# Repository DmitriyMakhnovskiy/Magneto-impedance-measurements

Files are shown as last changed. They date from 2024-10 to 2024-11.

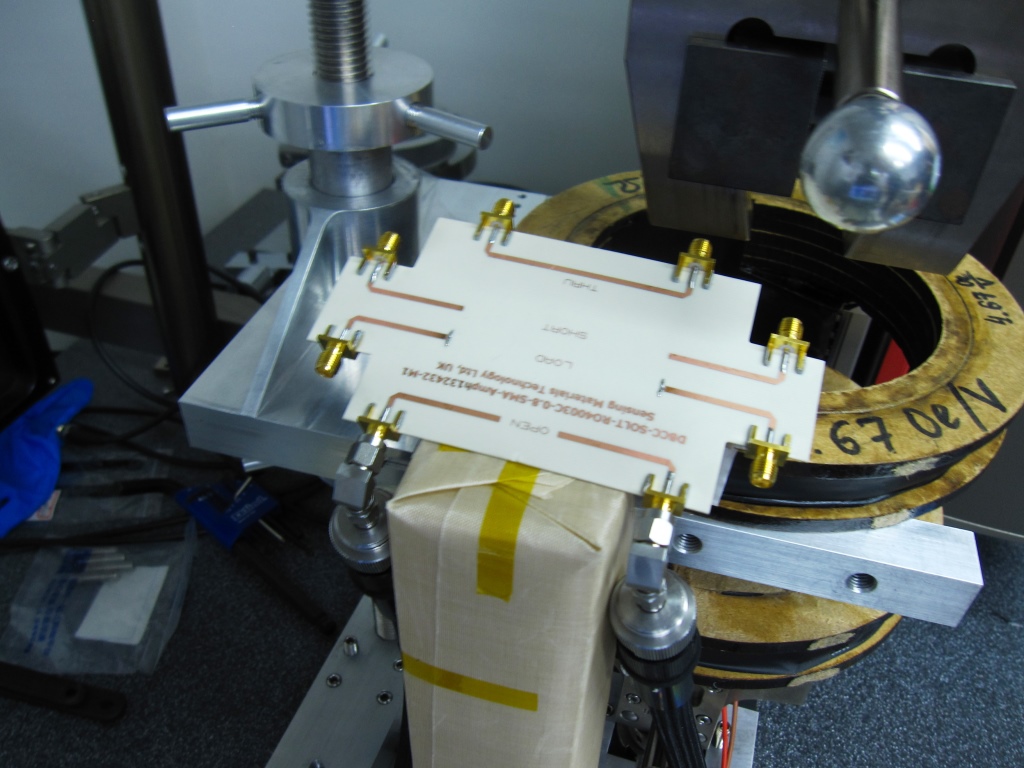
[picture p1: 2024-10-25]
Stress-impedance and Zwick-Roell Award/Design gallery/IMG_7724.JPG

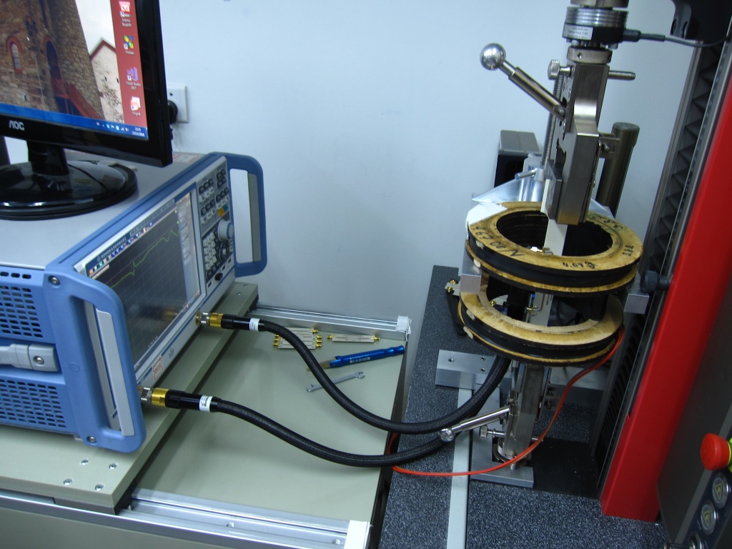
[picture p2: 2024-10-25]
Stress-impedance and Zwick-Roell Award/Design gallery/IMG_7733.JPG

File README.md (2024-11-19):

# Magneto-impedance_measurements
Measuring magneto-impedance in ferromagnetic wires subjected to external stimuli such as magnetic field, tensile stress, and temperature

See the report in the file "Report_Multi-stage calibration for impedance measurements.pdf". 

SUMMARY

This project focuses on measuring surface impedance in ferromagnetic wires, a crucial aspect in developing materials with specific microwave properties for applications in sensors and metamaterials. We present a broadband impedance measurement technique operational up to 15 GHz, designed to simplify the characterization of ferromagnetic microwires, which exhibit unique magnetic and conductive behaviors influencing electromagnetic scattering. We develop customized printed circuit board cells (see the folder Rogers' PCB cells) and a multi-stage calibration process that enables flexibility in testing under different external stimuli, such as magnetic fields, temperature, and mechanical stress.

KEY CONTRIBUTIONS

  Broadband Measurement Technique: Establishes a method for accurate impedance measurements up to 15 GHz, crucial for analyzing microwire-based composites.

  PCB Calibration Cells: Develops PCB cells for precise impedance measurements, accounting for factors like temperature and mechanical stress.

  Numerical Simulation Compatibility: Enables use of experimentally derived impedance values in computational simulations, supporting advanced material design.

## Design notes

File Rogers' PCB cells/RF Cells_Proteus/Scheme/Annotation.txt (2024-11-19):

Dogbone20
Material:RO4003C
Thickness: 0.8mm
Layers: Top copper, bottom copper, top silk
Mech3 layer repeats the board edge.

Sensing Materials Technology Ltd
contact@sensmattech.co.uk

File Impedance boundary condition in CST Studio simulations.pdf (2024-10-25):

# Use of the impedance boundary condition in CST Studio simulations

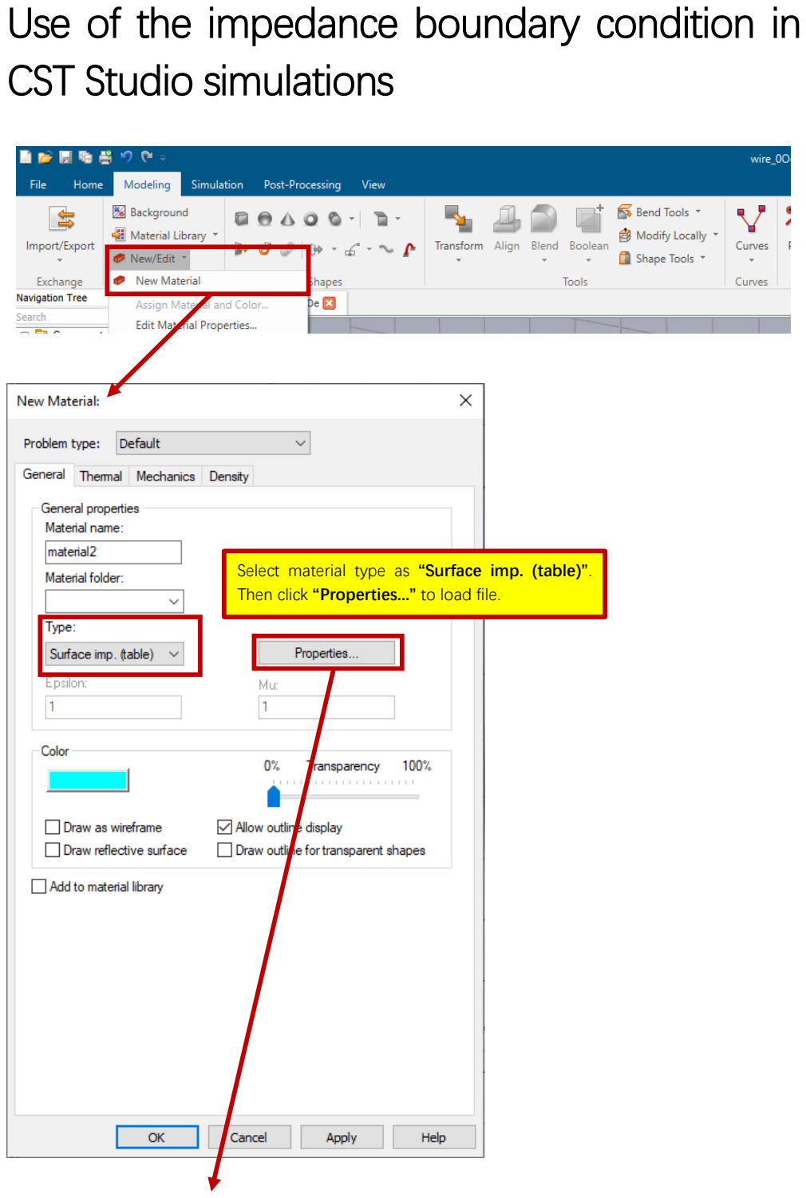
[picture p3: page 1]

Select material type as “Surface imp. (table)”. Then click “Properties...” to load file.

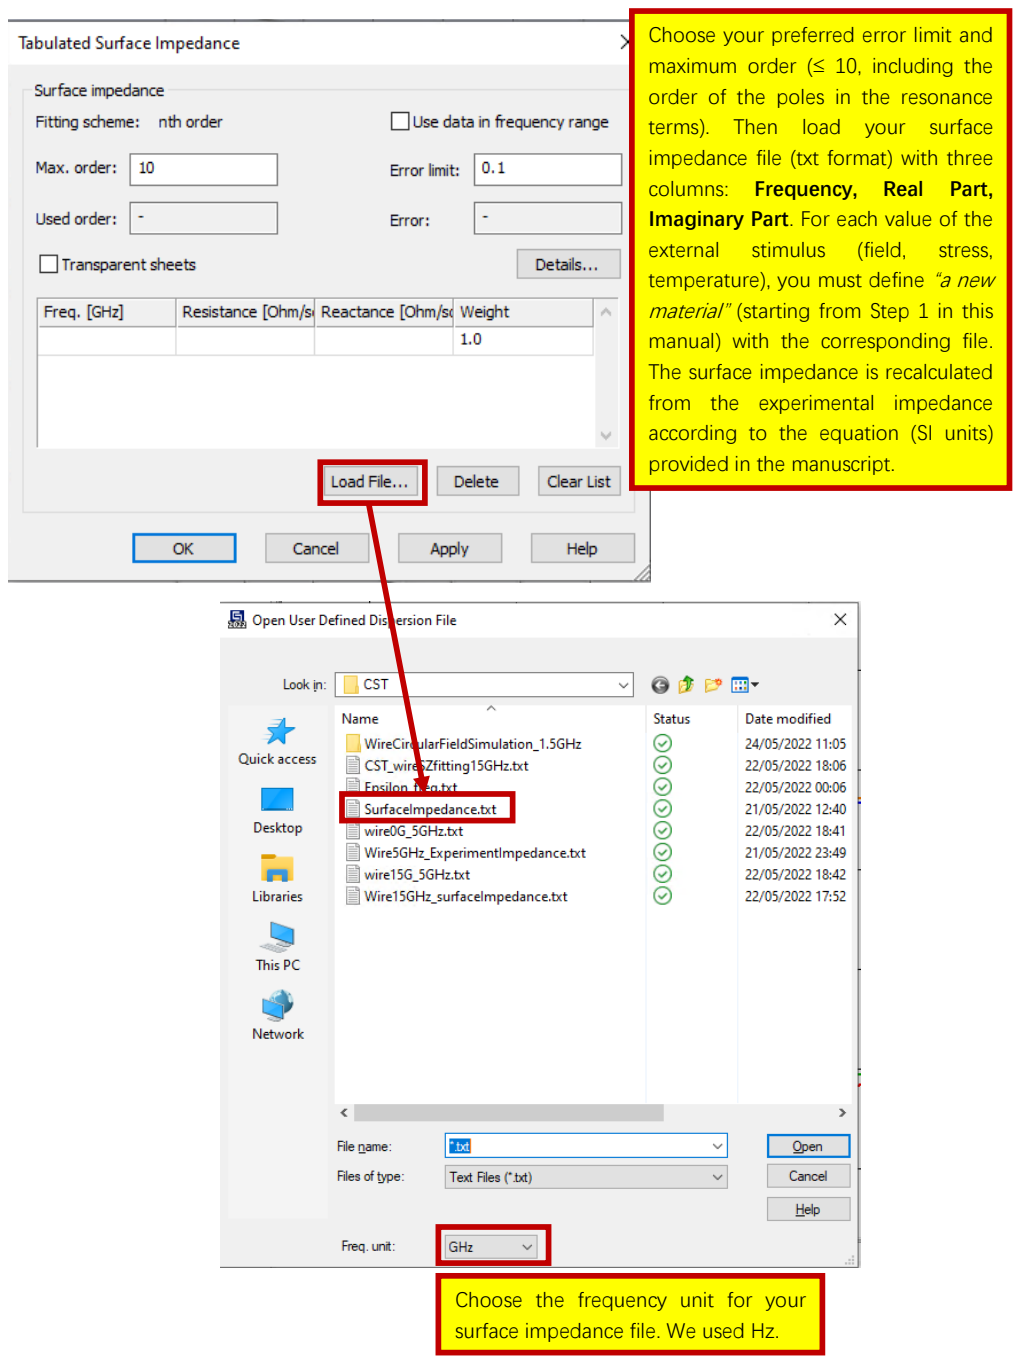
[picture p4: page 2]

Choose the frequency unit for your surface impedance file. We used Hz.

Choose your preferred error limit and maximum order (≤ 10, including the order of the poles in the resonance terms). Then load your surface impedance file (txt format) with three columns: Frequency, Real Part, Imaginary Part. For each value of the
external | stimulus | (field, | stress,
temperature), you must define “a new material” (starting from Step 1 in this manual) with the corresponding file. The surface impedance is recalculated from the experimental impedance according to the equation (SI units) provided in the manuscript.

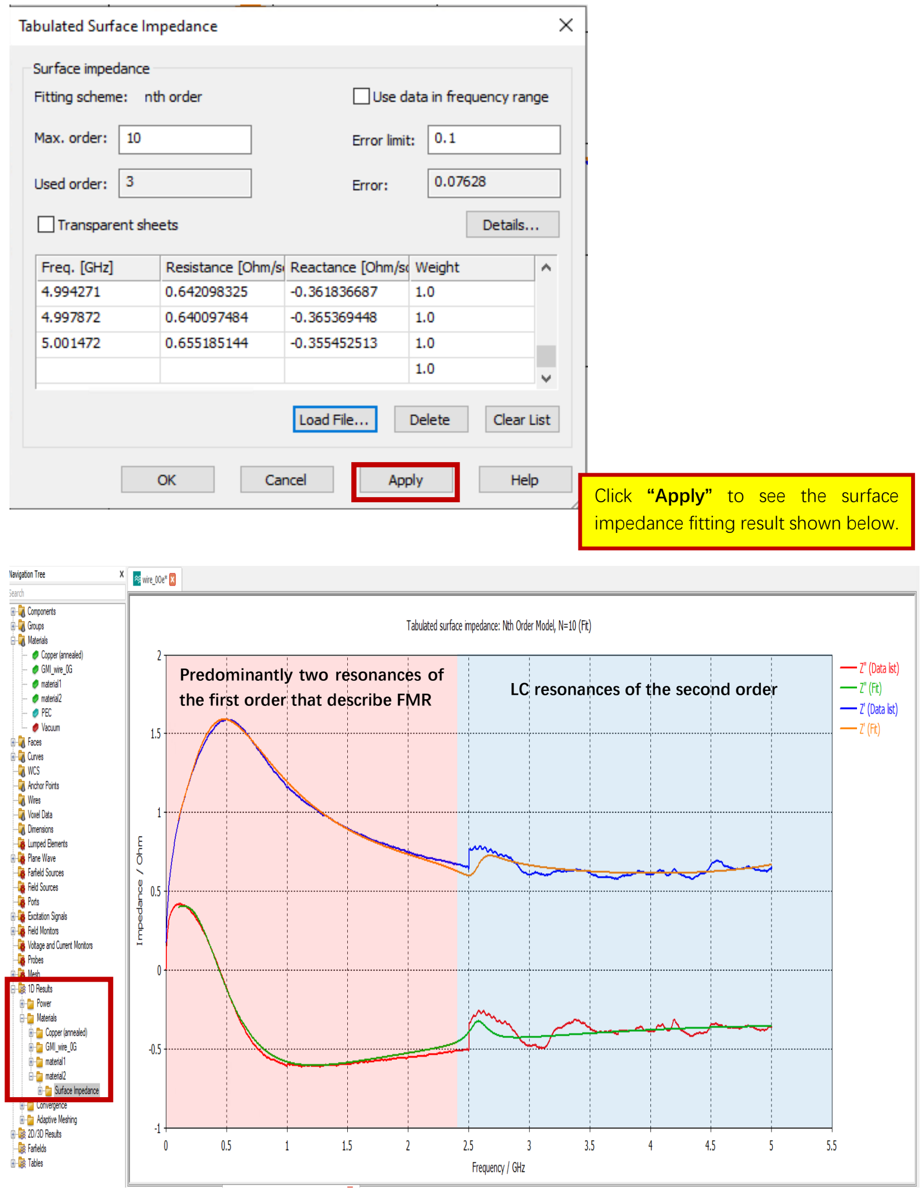
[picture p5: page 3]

Click “Apply” to see the surface impedance fitting result shown below.

Predominantly two resonances of
the first order that describe FMR | LC resonances of the second order

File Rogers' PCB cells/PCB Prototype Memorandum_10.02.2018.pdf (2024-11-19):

# PCB Prototype Memorandum

## Project

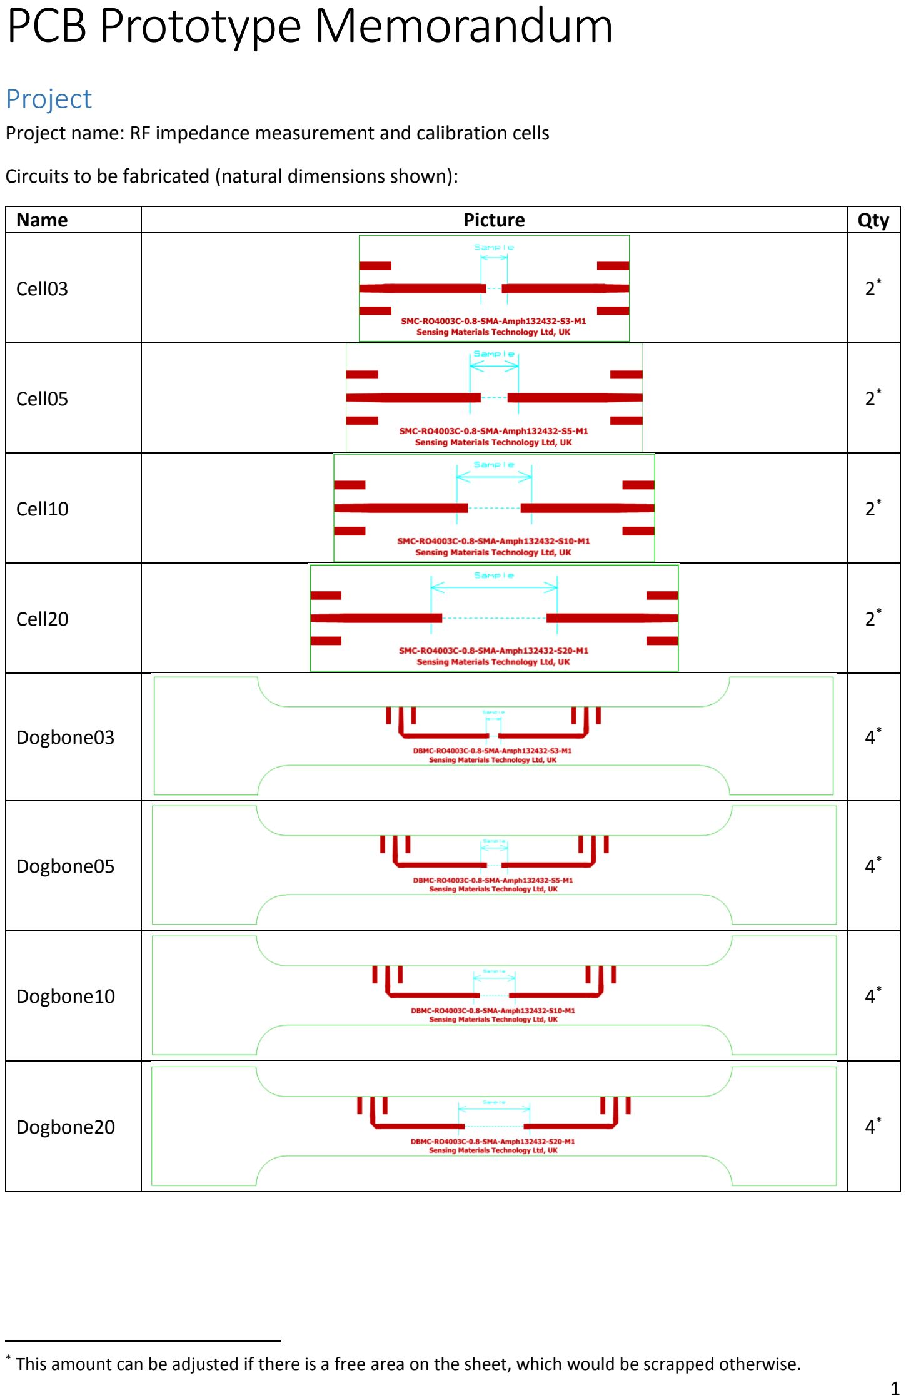
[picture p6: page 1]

Project name: RF impedance measurement and calibration cells

Circuits to be fabricated (natural dimensions shown):

Name | Picture | Qty
Cell03 | | 2 *
Cell05 | | 2 *
Cell10 | | 2 *
Cell20 | | * 2
Dogbone03 | | 4 *
Dogbone05 | | * 4
Dogbone10 | | 4 *
Dogbone20 | | 4 *

* This amount can be adjusted if there is a free area on the sheet, which would be scrapped otherwise.

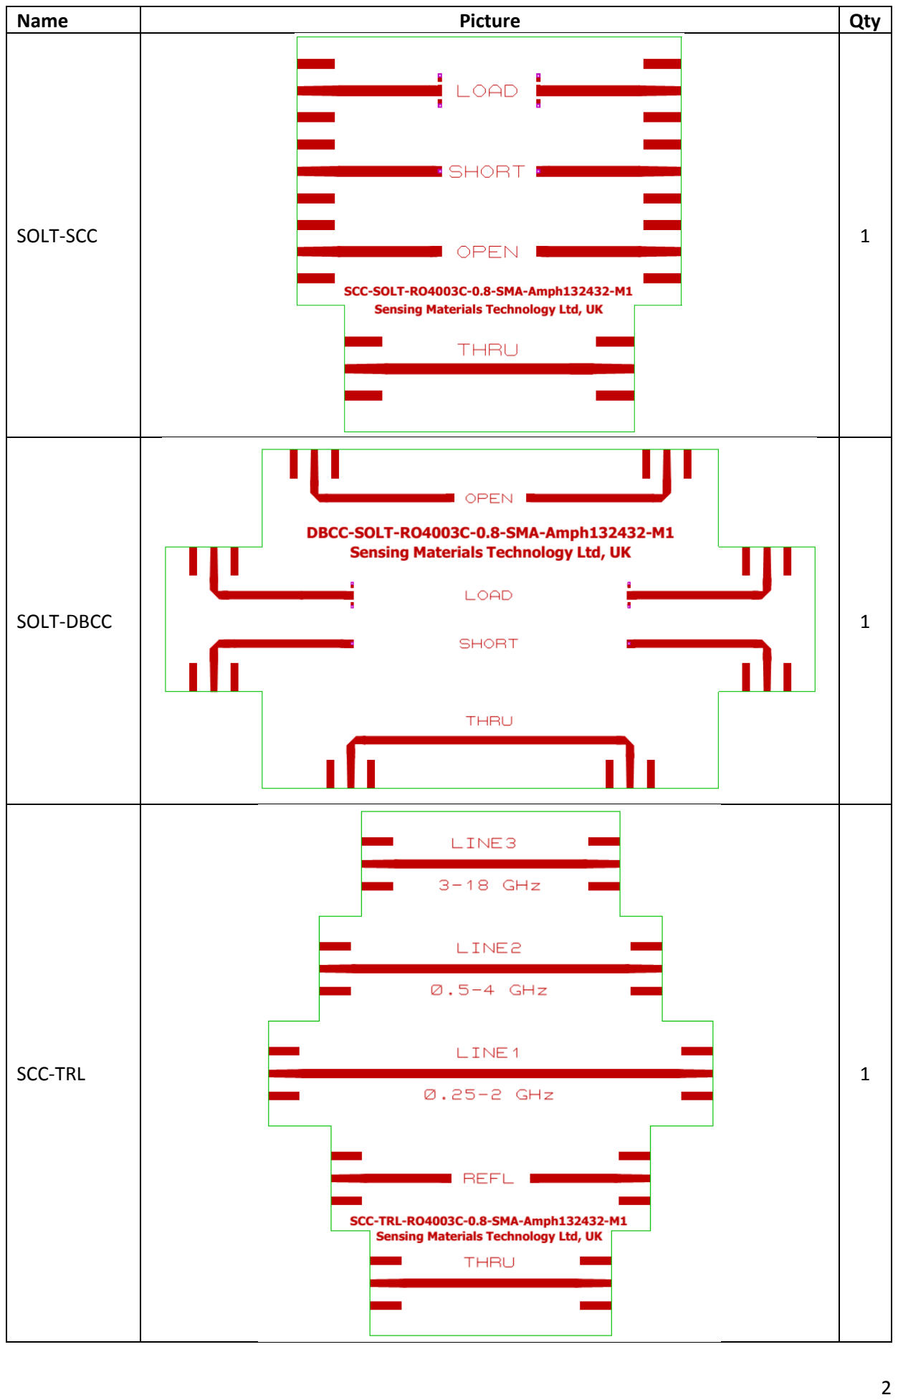
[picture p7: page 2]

Name | Picture | Qty
SOLT-SCC | | 1
SOLT-DBCC | | 1
SCC-TRL | 1

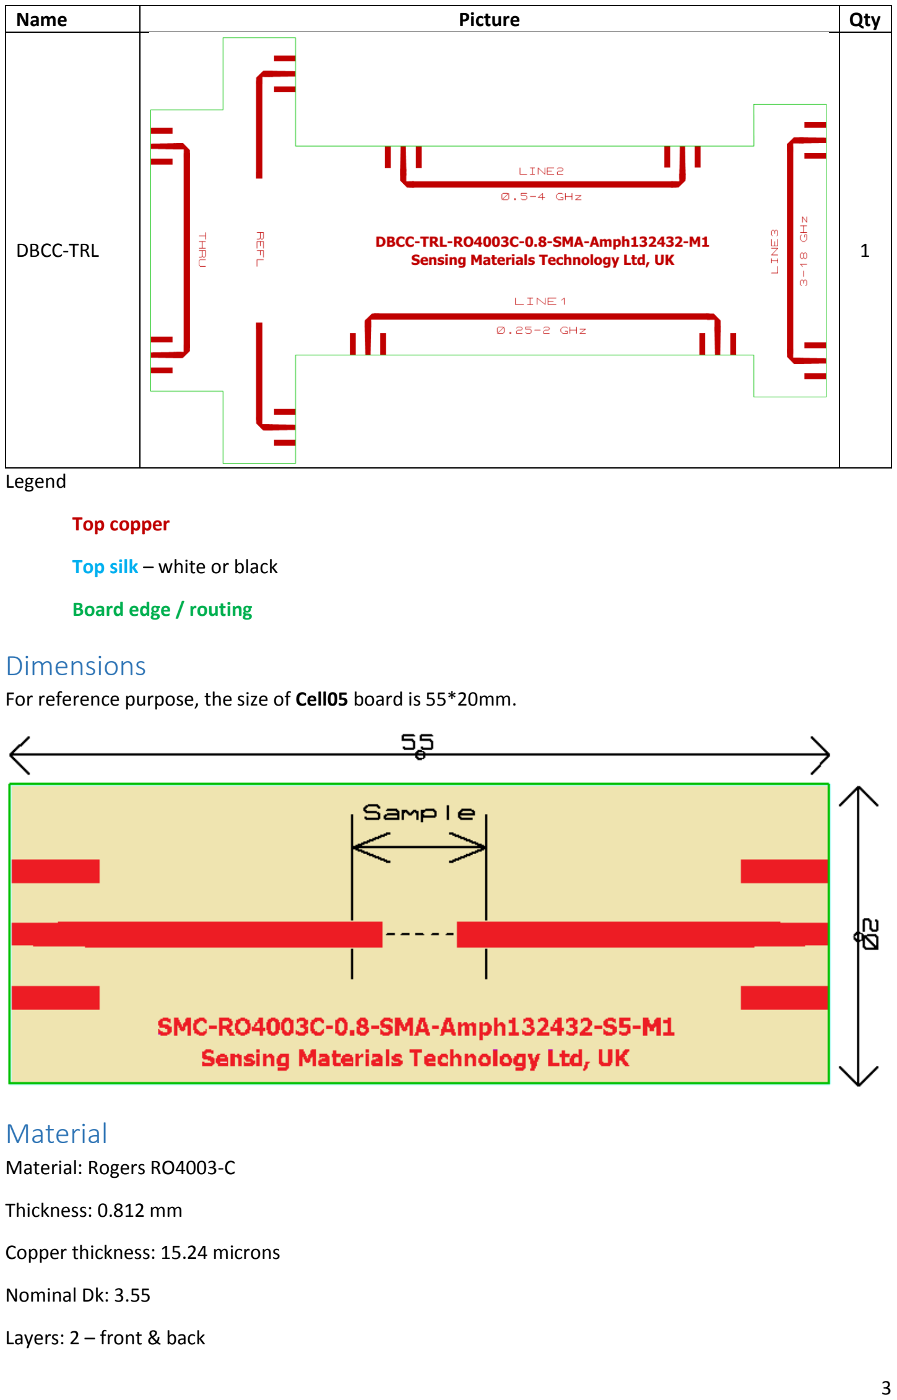
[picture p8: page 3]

Name | Picture | Qty
DBCC-TRL | | 1

Legend

Top copper

Top silk – white or black

Board edge / routing

## Dimensions

For reference purpose, the size of Cell05 board is 55*20mm.

## Material

Material: Rogers RO4003-C

Thickness: 0.812 mm

Copper thickness: 15.24 microns

Nominal Dk: 3.55

Layers: 2 – front & back

## PCB Fabrication

Surface finish: none

Silkscreen: single sided, front only, color depends on the color of the material: black for yellow or white for green.

Solder mask: none

Peelable mask: none

Carbon print: none

Carbon finish: none

Min. track width: 0.61 mm

Min track gap: standard

Vias: 0.3mm, plated, through

Shape: special contour routing

Electrical checks: not required

Data format: Gerber RS274X / RS264D, metric

## Panelizing

Gerber files for individual circuits would be provided. Panelizing is highly desirable.

## Other

Lead-time: 2 weeks

Delivery to: Plymouth, UK

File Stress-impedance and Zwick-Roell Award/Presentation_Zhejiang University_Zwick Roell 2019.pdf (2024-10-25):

# Integration of microwave and mechanical stress measurements:

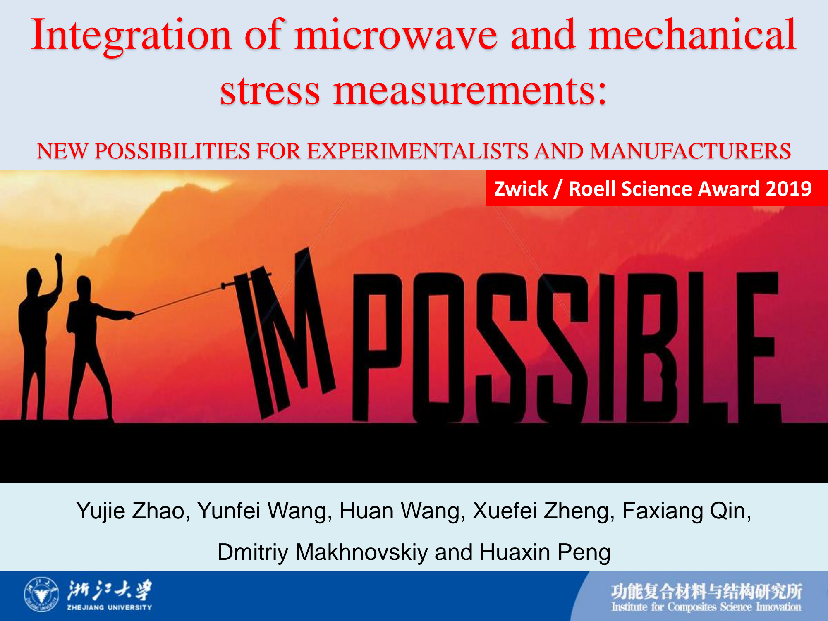
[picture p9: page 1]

NEW POSSIBILITIES FOR EXPERIMENTALISTS AND MANUFACTURERS

Yujie Zhao, Yunfei Wang, Huan Wang, Xuefei Zheng, Faxiang Qin,

Dmitriy Makhnovskiy and Huaxin Peng

Zwick / Roell Science Award 2019

# Content

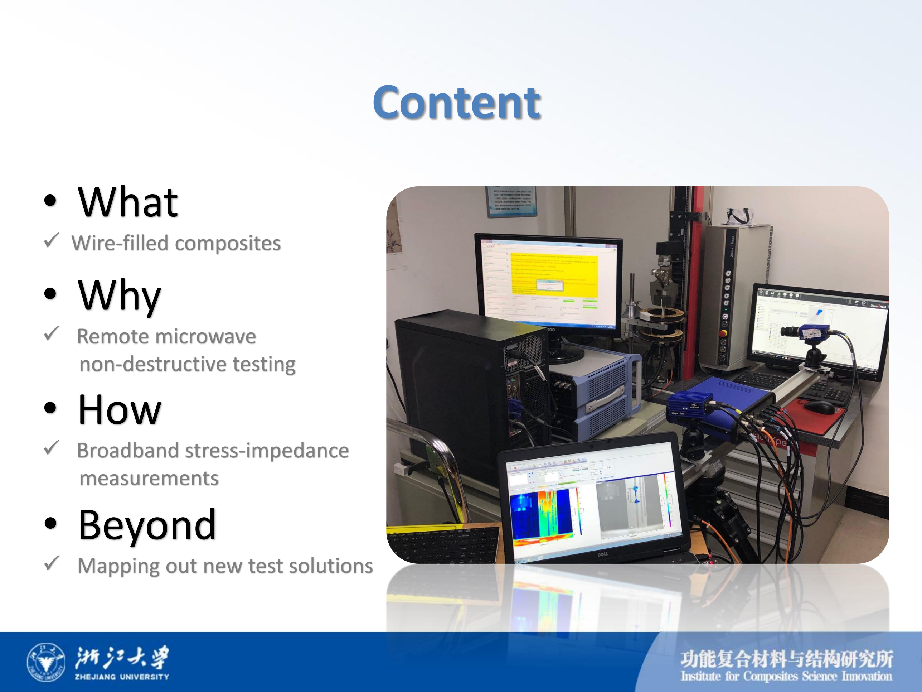
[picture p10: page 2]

# - What

✓ Wire-filled composites

# - Why

✓ Remote microwave
non-destructive testing

# - Beyond

✓ Mapping out new test solutions

# - How

✓ Broadband stress-impedance measurements

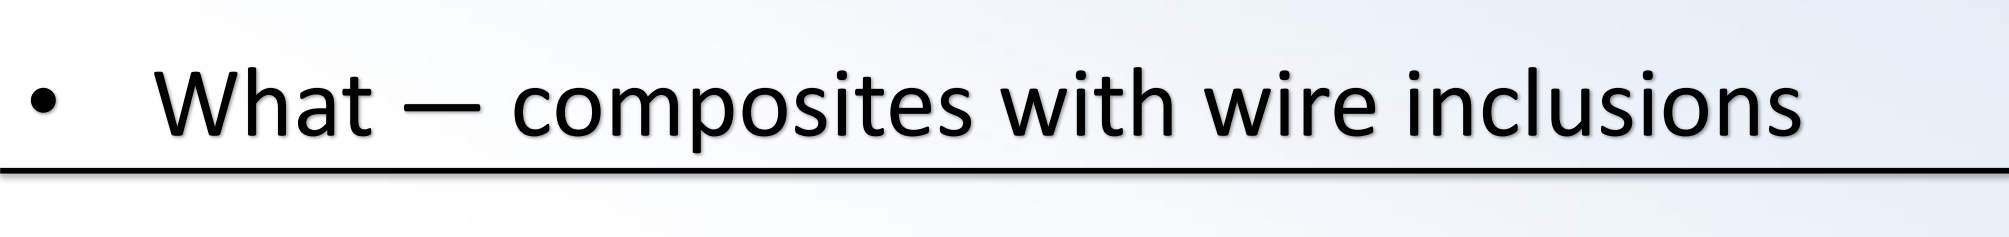
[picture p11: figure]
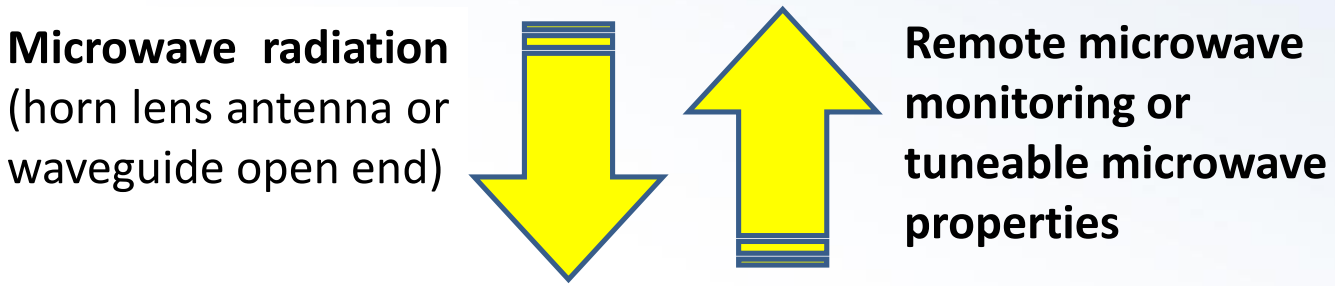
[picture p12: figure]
Microwave radiation (horn lens antenna or waveguide open end); Remote microwave monitoring or tuneable microwave properties
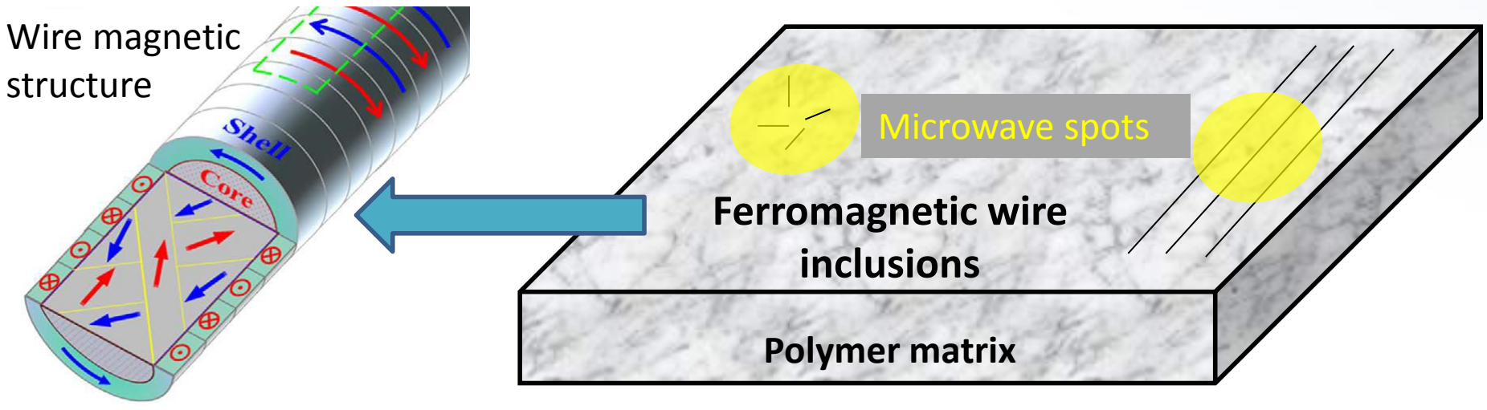
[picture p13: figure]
Ferromagnetic wire inclusions; Polymer matrix; Microwave spots; Wire magnetic structure

### External stimuli: magnetic field, mechanical stress, and temperature

# - What — composites with wire inclusions

# - Why—non-destructive evaluation technique

## Antenna

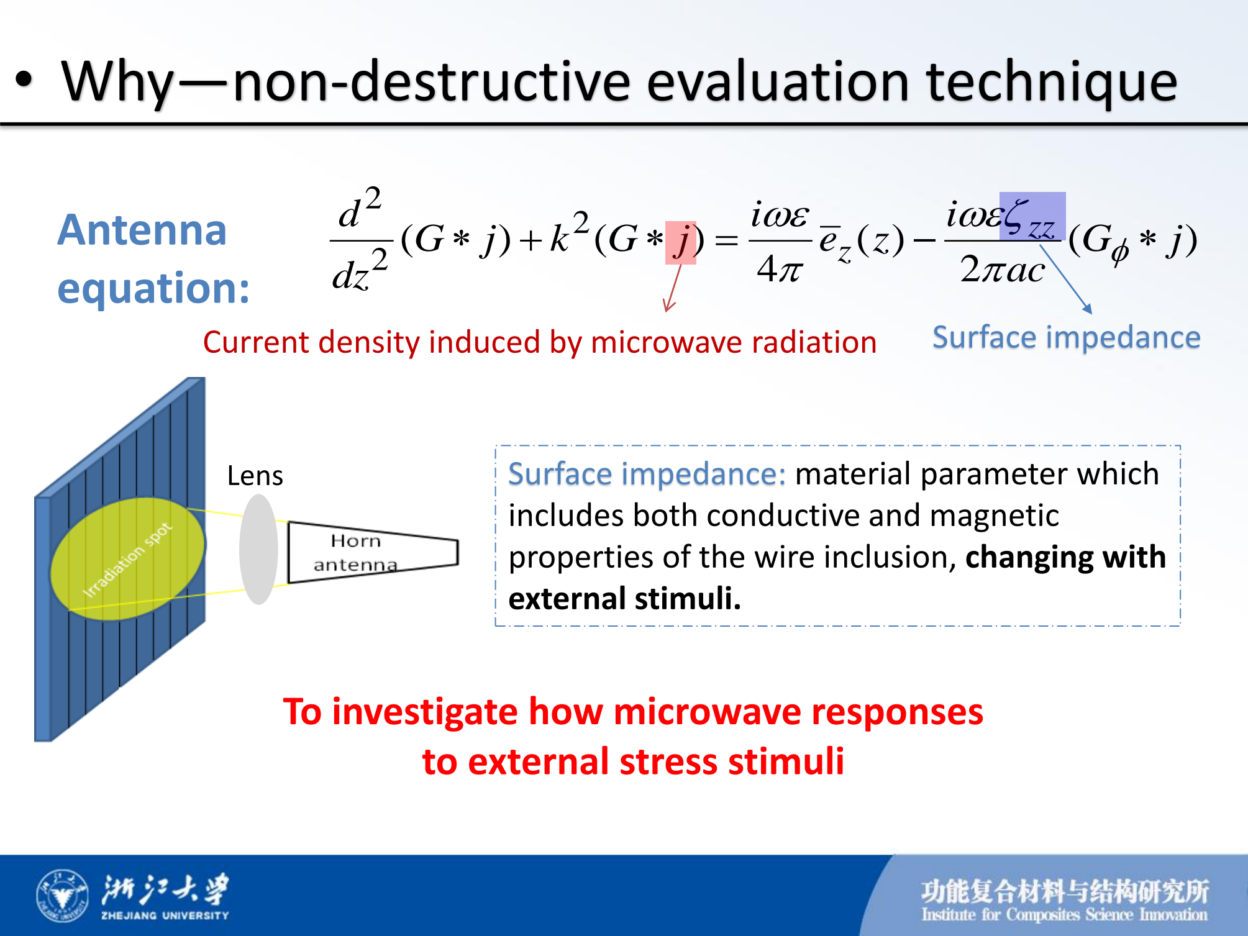
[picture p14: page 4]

2
2
2
( | ) | ( | ) | ( ) | ( | )
4 | 2

zz
z
d | i | i G j | k G | j | e z | G | j
dz | ac

φ

ωε | ωεζ
π | π
* | + | * | = | − | *
Current density induced by microwave radiation | Surface impedance
Lens | Surface impedance: material parameter which includes both conductive and magnetic properties of the wire inclusion, changing with external stimuli.

### To investigate how microwave responses to external stress stimuli

## equation:

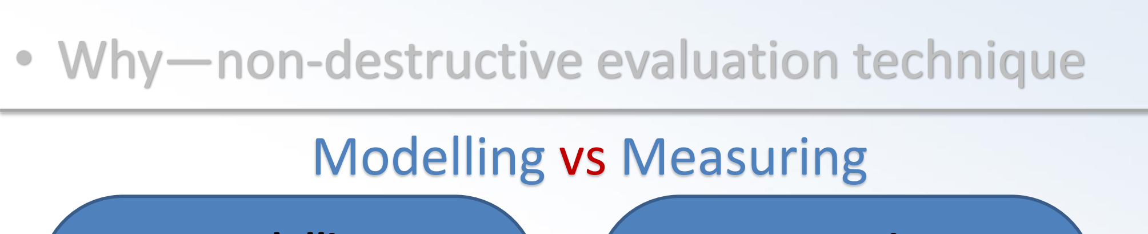
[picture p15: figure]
Modelling vs Measuring

# - Why—non-destructive evaluation technique

## Modelling

? ?

- Complicated magnetic domain structure
- Existing models are not
sufficiently accurate for
microwave scattering properties of composite structures

## Measuring

√ √

- Broad frequency range
calibration and measurement technique
- Recalculation into surface impedance by
- Develop scattering theory based on the antenna equation

9
( , , ) 10 | ( , , ) / (2 )
stress, | magnetic field
zz | H | aZ | H | cl
H
ζ ω | σ | ω | σ
σ

=
− | −

# - How—measurement system

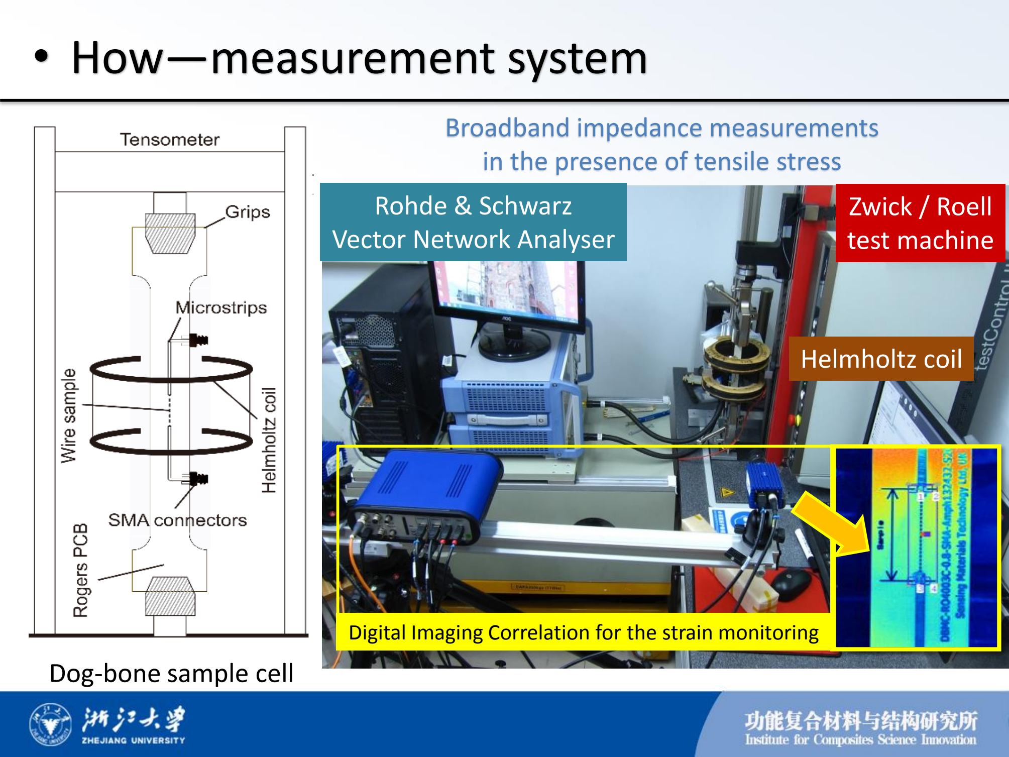
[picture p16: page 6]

Broadband impedance measurements in the presence of tensile stress Zwick / Roell
test machine

Rohde & Schwarz
Vector Network Analyser

Helmholtz coil

Dog-bone sample cell

Digital Imaging Correlation for the strain monitoring

# - How— RF calibration technique

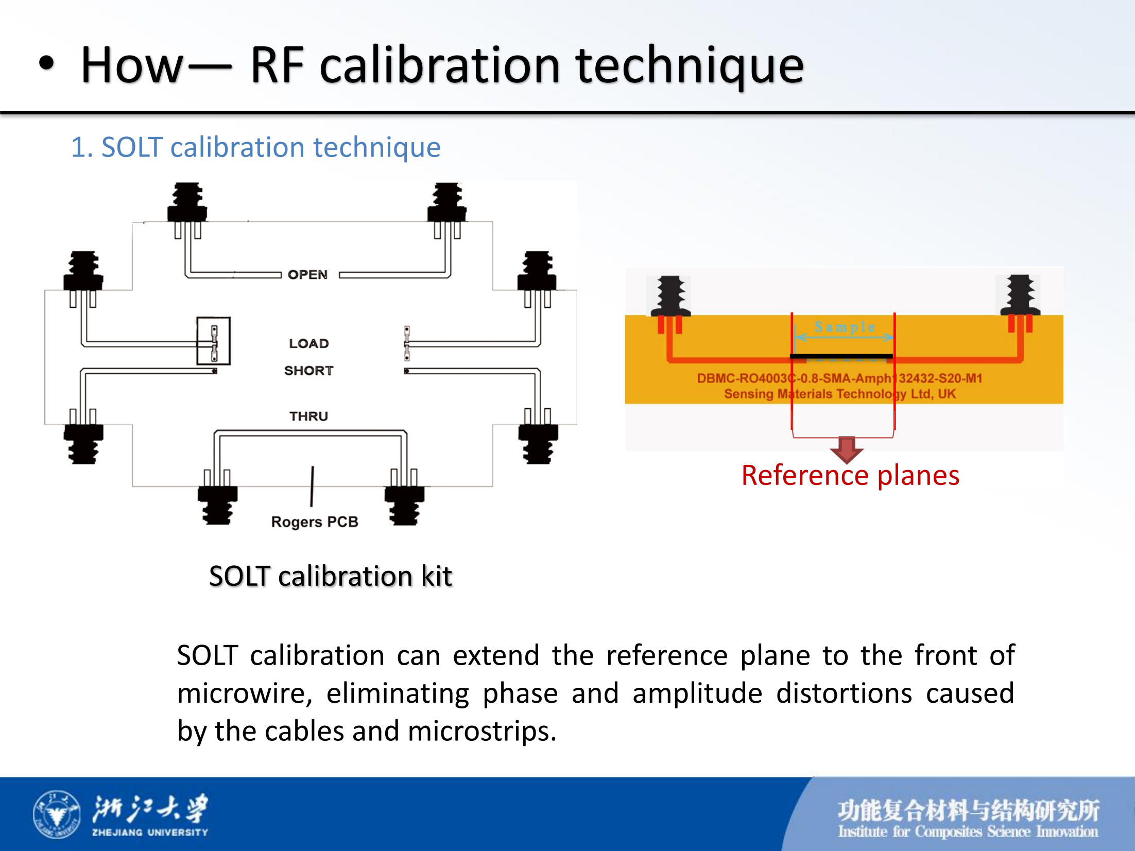
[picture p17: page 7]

SOLT calibration can extend the reference plane to the front of microwire, eliminating phase and amplitude distortions caused by the cables and microstrips.

Reference planes

1. SOLT calibration technique

SOLT calibration kit

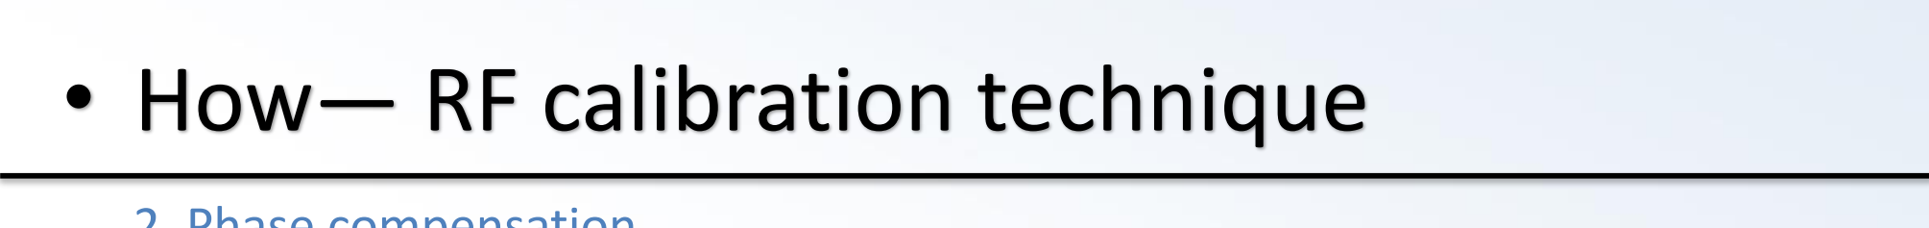
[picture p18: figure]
• How— RF calibration technique

2. Phase compensation

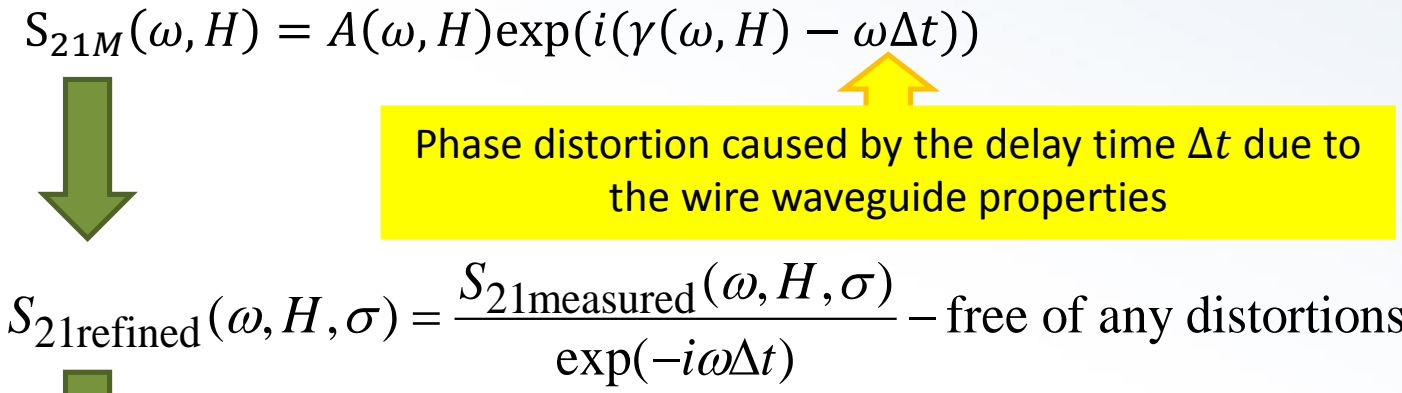
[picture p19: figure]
S21M ω, H = A ω, H exp(i(γ ω, H − ω∆t)); the wire waveguide properties; 21measured; 21refined

Phase distortion caused by the delay time ∆t due to

### microwave-stress correlation !!!

( , , ) ζ ω | σ zz | H

2
2
2
( | ) | ( | ) | ( | ) 4 | 2

zz
z
d | i | i G j | k G j | e | G | j
dz | ac

φ

ωε | ωεζ
π | π
* | + | * | = | − | *
( , , ) ( , , ) | free of any distortions exp( | )

21refined

21refined

100 (1 | ( , , )) ( , , ) | impedance free of any distortions
( , , )
S | H Z | H
S | H
ω | σ
ω | σ
ω | σ

×−
= | −

# - How—automatic measurement system

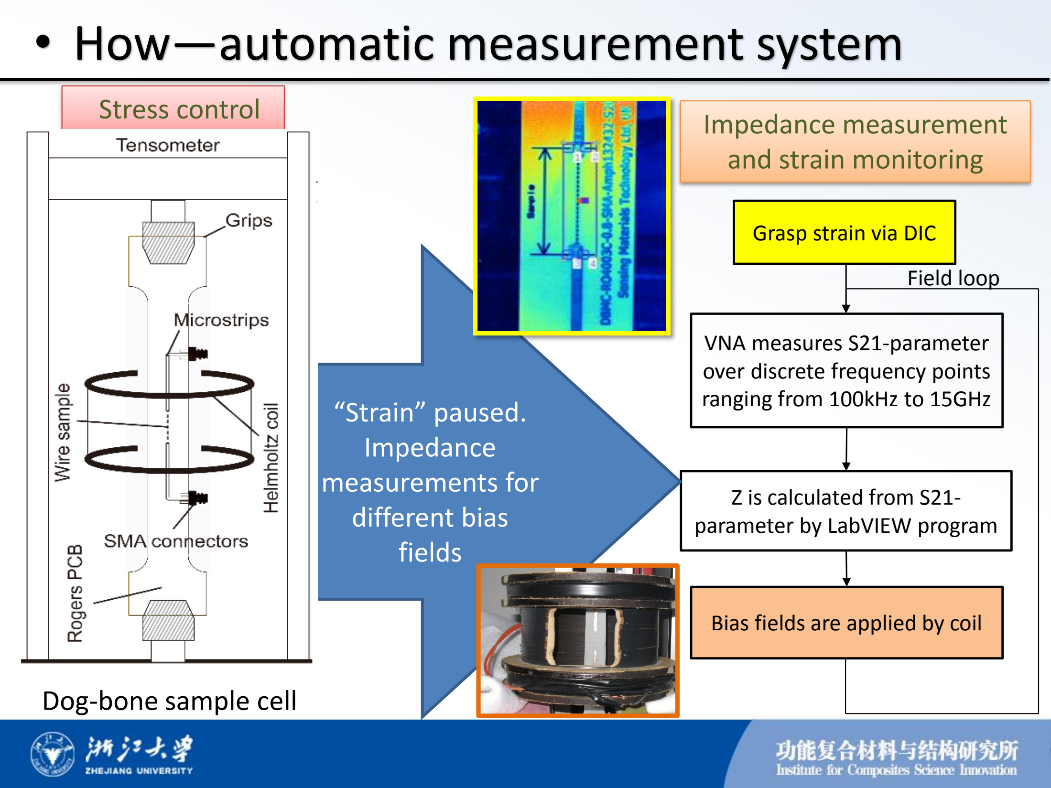
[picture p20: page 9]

Stress control | Impedance measurement
| and strain monitoring
| Grasp strain via DIC

VNA measures S21-parameter over discrete frequency points ranging from 100kHz to 15GHz

Z is calculated from S21-
parameter by LabVIEW program

Bias fields are applied by coil

Field loop

“Strain” paused.
Impedance
measurements for
different bias
fields

Dog-bone sample cell

## Broadband magneto- and stress-impedance measurements

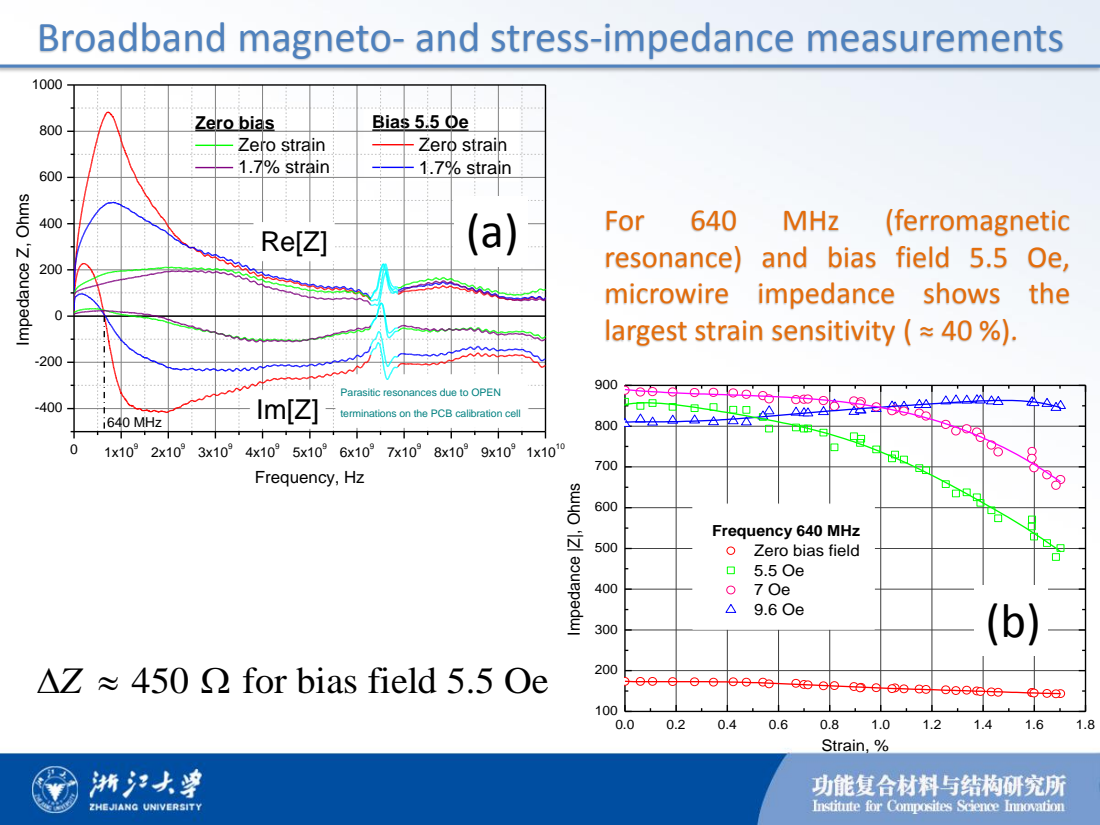
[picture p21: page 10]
Strain, %; Bias 5.5 Oe Zero strain 1.7% strain; Zero bias Zero strain 1.7% strain; Frequency, Hz; 640 MHz; for bias field 5.5 Oe; For; MHz; (ferromagnetic

terminations on the PCB calibration cell Impedance Z, Ohms

resonance) and bias field 5.5 Oe,
microwire impedance shows the
largest strain sensitivity ( ≈ 40 %).

Parasitic resonances due to OPEN

Frequency 640 MHz | 9.6 | Oe Impedance |Z|, Ohms

Zero bias 5.5 7 Oe | Oe | field

# - Beyond—Integration of microwave measurements with multi-stimuli

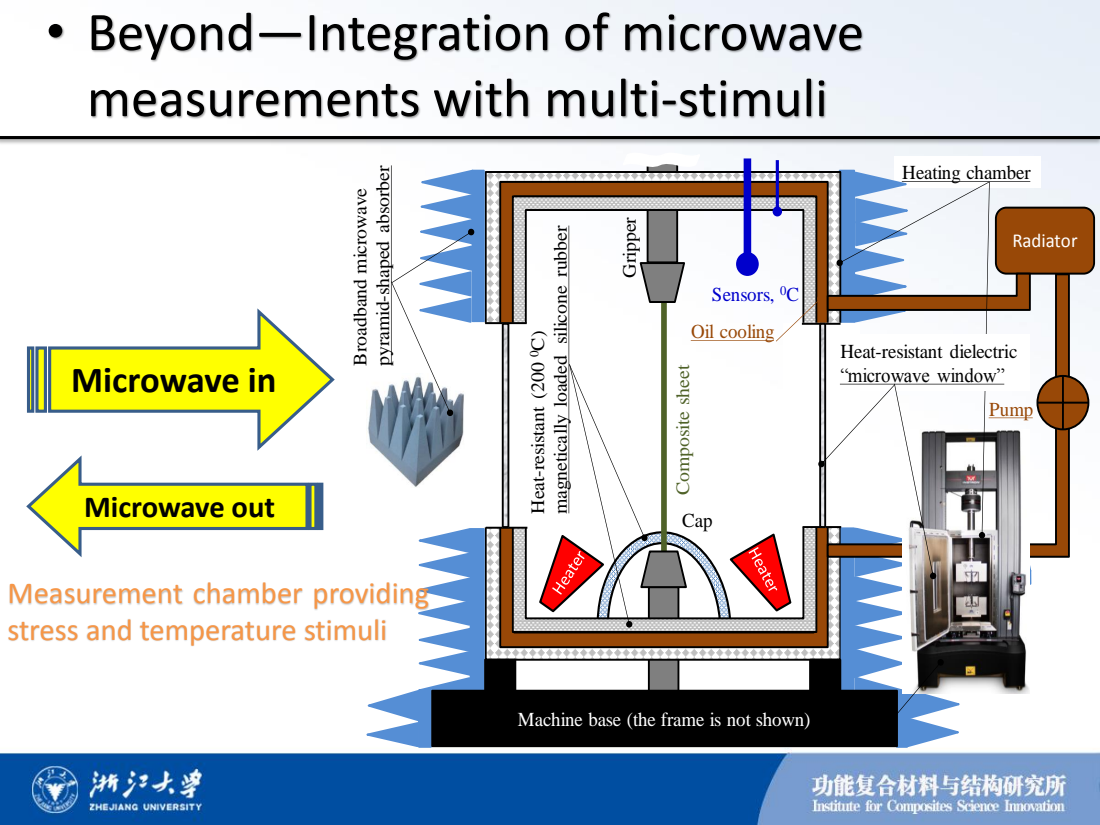
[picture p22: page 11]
Cap; Oil cooling; Radiator; Pump; Sensors, 0C; Microwave in; Microwave out

Broadband microwave pyramid-shaped absorber

Heating chamber Heat-resistant (200

Machine base (the frame is not shown) Gripper

0C) magnetically loaded silicone rubber Composite sheet

Heat-resistant dielectric
“microwave window”

Measurement chamber providing
stress and temperature stimuli

# Industry and academia cooperation

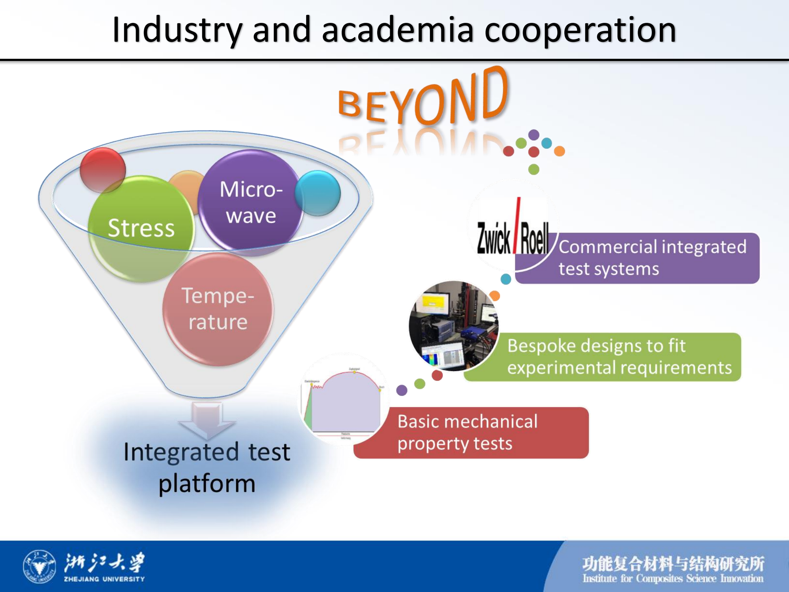
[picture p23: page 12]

# Thank you

## With best wishes from Hangzhou

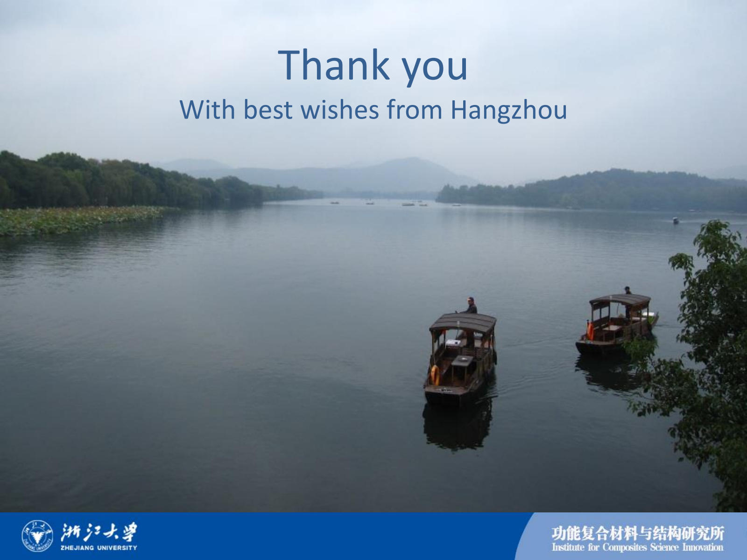
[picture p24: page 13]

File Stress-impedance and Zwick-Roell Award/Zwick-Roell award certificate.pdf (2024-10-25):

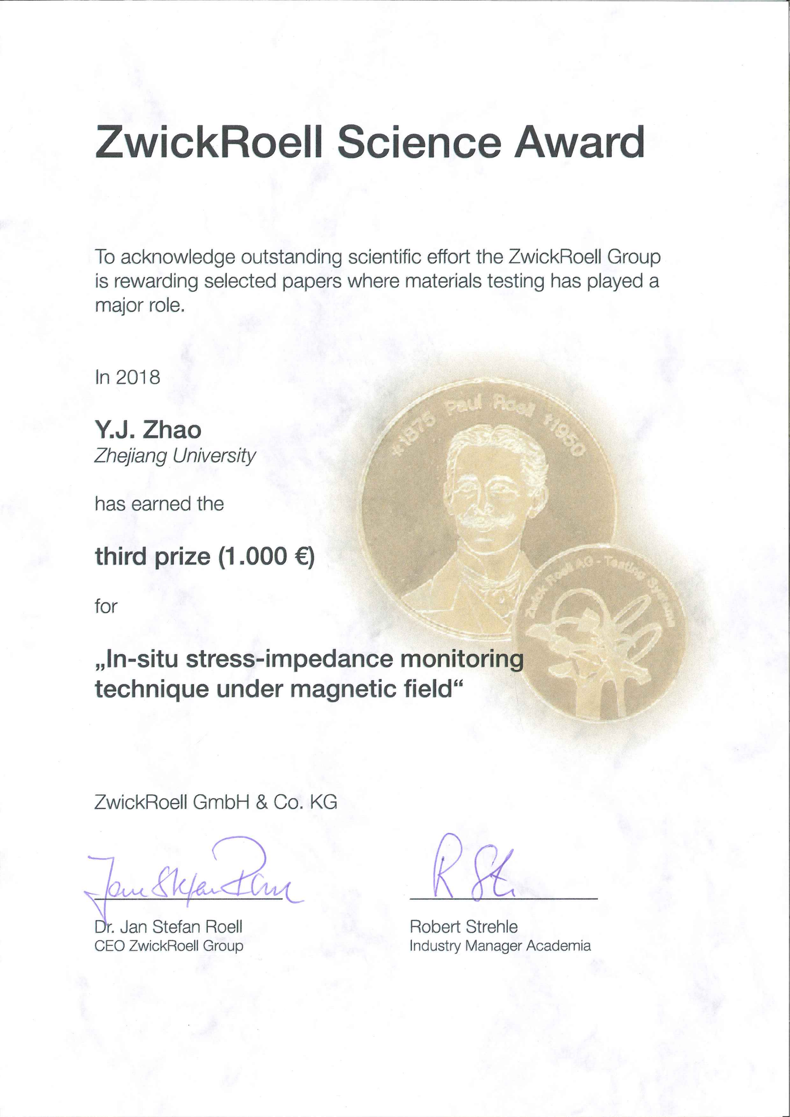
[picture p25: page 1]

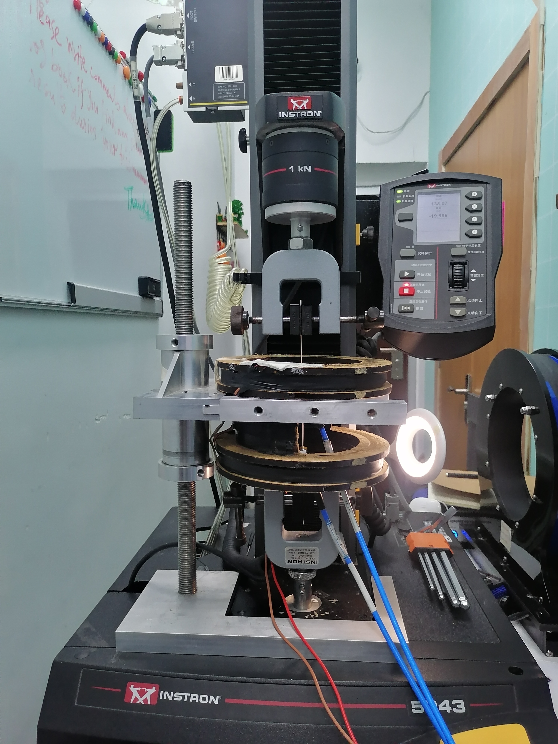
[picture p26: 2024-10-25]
Design_gallery/mmexport1635602847087.jpg

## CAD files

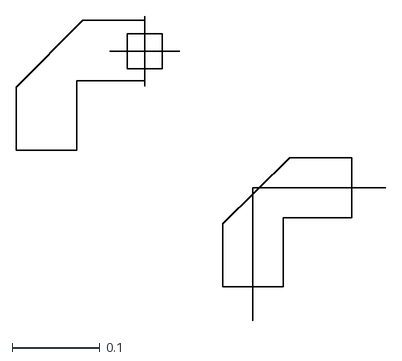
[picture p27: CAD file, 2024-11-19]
Rogers' PCB cells/RF Cells_Proteus/Scheme/Angle.DXF
0.422 x 0.348

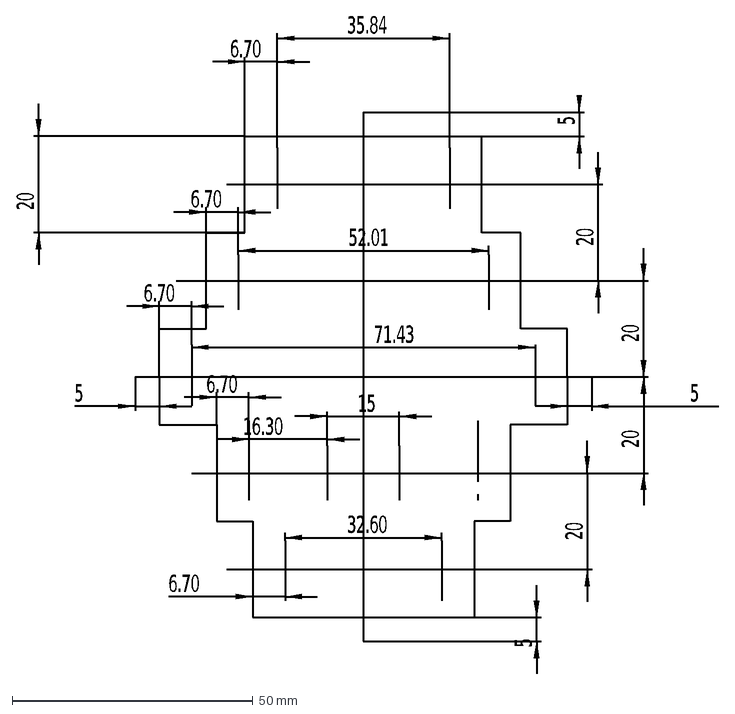
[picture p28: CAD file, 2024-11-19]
Rogers' PCB cells/RF Cells_Proteus/Scheme/SCC-TRL.DXF
20
35.84
6.70
52.01
71.43
15
16.30
32.60
5

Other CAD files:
Rogers' PCB cells/RF Cells_Proteus/Scheme/Angle.SLDDRW
Rogers' PCB cells/RF Cells_Proteus/Scheme/DBCC-TRL.SLDDRW
Rogers' PCB cells/RF Cells_Proteus/Scheme/SCC-TRL.SLDDRW

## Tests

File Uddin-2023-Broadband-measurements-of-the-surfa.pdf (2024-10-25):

### Measurement Science and Technology

ACCEPTED MANUSCRIPT

## Broadband measurements of the surface impedance in ferromagnetic wires as a boundary condition for scattering problems

To cite this article before publication: Azim Uddin et al 2023 Meas. Sci. Technol. in press https://doi.org/10.1088/1361-6501/accd09

### Manuscript version: Accepted Manuscript

Accepted Manuscript is “the version of the article accepted for publication including all changes made as a result of the peer review process, and which may also include the addition to the article by IOP Publishing of a header, an article ID, a cover sheet and/or an ‘Accepted Manuscript’ watermark, but excluding any other editing, typesetting or other changes made by IOP Publishing and/or its licensors”

This Accepted Manuscript is © 2023 IOP Publishing Ltd.

During the embargo period (the 12 month period from the publication of the Version of Record of this article), the Accepted Manuscript is fully protected by copyright and cannot be reused or reposted elsewhere.

As the Version of Record of this article is going to be / has been published on a subscription basis, this Accepted Manuscript will be available for reuse under a CC BY-NC-ND 3.0 licence after the 12 month embargo period.

After the embargo period, everyone is permitted to use copy and redistribute this article for non-commercial purposes only, provided that they adhere to all the terms of the licence https://creativecommons.org/licences/by-nc-nd/3.0

Although reasonable endeavours have been taken to obtain all necessary permissions from third parties to include their copyrighted content within this article, their full citation and copyright line may not be present in this Accepted Manuscript version. Before using any content from this article, please refer to the Version of Record on IOPscience once published for full citation and copyright details, as permissions may be required. All third party content is fully copyright protected, unless specifically stated otherwise in the figure caption in the Version of Record.

View the article online (https://doi.org/10.1088/1361-6501/accd09) for updates and enhancements.

This content was downloaded from IP address 138.251.14.35 on 17/04/2023 at 21:42

1 | Broadband measurements of the surface impedance in ferromagnetic wires
2 | as a boundary condition for scattering problems

3
| Azim Uddin¹⁾ , Faxiang Qin¹,*) , Diana Estevez¹,2) , Konstantin Gorbatov³⁾ , Yujie Zhao⁴⁾
4 | , and
| Dmitriy Makhnovskiy⁵⁾
5

6

1) 7 | Institute for Composites Science Innovation (InCSI), School of Materials Science & Engineering,
8 | Zhejiang University, 38 Zheda Road, Hangzhou, 310027, China.
2) 9 | Ningbo Innovation Centre, Zhejiang University, 1 South Qianhu Road, Ningbo, 315100, China.
| 3)
10 | Lisi Aerospace, 38 Butlers Leap, Rugby, Warks CV21 3RQ, England.
| 4)
11 | School of Physics and Astronomy, University of St. Andrews, Fife KY16 9SS, Scotland.
| 5)
12 | Sensing Materials Technology Ltd, 44 St. Michael’s Close, Plymouth, Devon PL1 4RX, England.
13
14 | First author: auddin@zju.edu.cn
*) 15 | Corresponding author: faxiangqin@zju.edu.cn
16
17 | Abstract
18 | In the cm-wave range, the skin depth is comparable to the micron radius of
19 | ferromagnetic wires and thus their magnetic and conductive properties will influence the
20 | scattered electromagnetic field. Solving the scattering problem by considering the complicated
21 | internal magnetic structure of the wire becomes unpractical. There is a need to develop hybrid
22 | methods when the external problem of scattering on an inclusion is solved together with the
23 | experimental impedance conditions on its surface. Herein, we propose an accurate broadband
24 | impedance measurement technique operating up to 15 GHz. The PCB measurement and
25 | calibration cells designed in this work allow flexibility in choosing external stimuli such as
26 | magnetic field, tensile stress, and heat. The experimental impedance can be then used as the
27 | boundary condition in electromagnetic simulations making it possible to model, predict and
28 | design wire-based composites using numerical solvers such as CST Studio Suite.

29

30 | Keywords: Impedance boundary condition; Ferromagnetic microwires; Network calibration;
31 | De-embedding; Microwave scattering; PCB cells.

32

Page 1 of 28 | AUTHOR SUBMITTED MANUSCRIPT - MST-116463.R1

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
# 60 Accepted Manuscript

33 | 1. Introduction
34 | Dynamic magnetic behaviour through magnetoimpedance (MI) effect [1] is an essential
35 | property to characterize the microwave response of different materials such as ferromagnetic
36 | microwires [2-6], ribbons [7], and thin films [8-10]. Apart from fundamental research interest,
37 | in the technological context materials exhibiting a large MI effect arise as field/stress-sensitive
38 | sensors that can be integrated into a wide range of devices [11-16]. Special emphasis has been
39 | placed on Co-based and Fe-based glass-coated microwires. The thin glass shell (2 − 15
40 | microns) along with the magnetostriction (positive or negative) of the core alloy (diameter 5 −
41 | 30 microns) determine their unique magnetic anisotropic and mechanical properties. The
42 | technology of continuous casting of such wires makes it possible to produce highly-flexible
43 | threads of kilometre length [17]. These features allow them to be used as functional fillers in
44 | composite materials to introduce electromagnetic functionalities in the microwave range (ultra-
45 | high frequency UHF and super high frequency SHF bands), such as field/stress tunability,
46 | cloaking, absorption and shielding [18-24]. Such plethora of functional materials and their
47 | increasing trend towards operating at broader bandwidth stimulate the development of accurate
48 | measurement techniques to characterize their MI and microwave behaviour. The most
49 | commonly used methods are based on shorted coaxial transmission lines [25-27], microstrip
50 | transmission lines (MTLs) and coplanar waveguides (CPWs) etched on printed circuit boards
51 | (PCB) [28-32] aided by vector network analysers (VNA). In the shorted coaxial lines, one end
52 | of the microwire is connected to the inner conductor, while the other end is connected to the
53 | ground of the coaxial cap. The alignment of the sample along the axis will determine the
54 | measurement accuracy. Except for testing under magnetic field, measurements with sample
55 | stretching or heating are hardly possible in such coaxial cells. MTLs consist of a metal-backed
56 | substrate of relative permittivity εr on top of which is a metal strip with its width determined
57 | by the characteristic impedance of the line [33]. The sample is usually mounted on the surface
58 | of a PCB in the gap between two aligned microstrips and connected to them by soldering or
59 | conducting painting/glue. This method works for elongated samples of various geometries
60 | (wire, film, or ribbon), which can be considered as a continuation of a microstrip waveguide,
61 | although with a different characteristic impedance. Mounting the sample on the surface of PCB
62 | allows the application of external stimuli, including magnetic field, heat, and tensile stress.
63 | Meanwhile, the CPW PCB cells have an additional ground plane on the side of the microstrips
64 | that improves signal integrity at higher frequencies. This plane is also convenient for adding
65 | shunt surface elements, such as SHORT and LOAD terminations, which can be used for
AUTHOR SUBMITTED MANUSCRIPT - MST-116463.R1 | Page 2 of 28

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
# 60 Accepted Manuscript

calibration of the microstrip network. The CPW cells are suitable for another measurement

scheme where a thin and sufficiently wide sample (film or ribbon) is placed over the continuous

strip, covering only its central segment. Direct electrical contact with the strip is excluded by

introducing a subtle gap or isolating layer. The parameter of interest is no longer the impedance

of the sample itself, but its magnetic and dielectric properties, determined indirectly through

the measurement of S-parameters of the loaded waveguide segment [28].

VNA, coaxial cables, non-coaxial strips on PCB, and a non-lumped sample constitute

a cascaded network that requires a multi-stage calibration procedure. The ultimate goal is to

extend the reference plane directly to the sample. VNA and the cables can be calibrated using

the standard 12-term error correction model with the coaxial SHORT-OPEN-LOAD-THRU

(SOLT) terminations. The strip waveguides must be de-embedded based on different methods

[28,30,31,34]. In turn, an elongated sample over a continuous ground (or segment of a loaded

strip) constitutes a structure which waveguide properties must be considered when calculating

material parameters from the S-parameter measurements. The principles of multi-stage

calibration have already been implemented for thin film samples, where ferromagnetic

resonance (FMR) and permeability dispersion were of primary interest [28,31]. The study of

Bilzer et al. [28] is closely related to the method developed in our present work since the

waveguide properties of the loaded CPW segment were explicitly revealed there. The

measurements were carried out up to 14 GHz, which is of interest for microwave scattering

applications. However, this method requires an additional reference measurement when the

film sample is removed leaving a continuous strip, and thus cannot be applied to a wire sample.

In another method proposed by Gonzalez et al. [31], a thin film sample was electrically attached

to microstrips on the PCB surface. It was assumed that the per-unit-length resistance and

inductance (used as indicative parameters characterising FMR), could be derived from the

measured characteristic impedance and propagation exponent. However, it remained unclear

how the shunt capacitance and conductance (per unit length) were estimated, which are

required to solve the corresponding equations. The maximum measurement frequency was up

to only 3 GHz, which, given the sample length used (11 mm), does not allow to judge the

accuracy of the phase distortion compensation along the sample. A radical decrease in sample

length enables considering the sample as a lumped element without a phase incursion even at

higher GHz. Such measurements have been performed with short wires connected at the end

of an open coaxial connector between the core and the ground shell [35,36]. However, in very

short samples, the magnetic domain structure at the ends might significantly change both the

magnetostatic and high-frequency properties. Moreover, due to open-end parasitic capacitance

Page 3 of 28 | AUTHOR SUBMITTED MANUSCRIPT - MST-116463.R1

# 60 Accepted Manuscript

and radiation losses (which are not included in the calibration), the accuracy of impedance

measurements will deteriorate.

In this work, we develop a broadband method for measuring accurately the field and

stress dependencies of the surface impedance in ferromagnetic wires. The measurements in the

frequency range up to 15 GHz were performed on MTL cells. In contrast to Bilzer and

Gonzalez [28,31], the part of the network formed by the microstrip and the coaxial connector

on PCB was not assumed to be ideal. Its 3-term model was created using a calibration cell

where three reflection coefficients were measured from identical microstrips with surface

mount SOL terminations. Touchstone S1P files containing the reflection coefficients were then

created for such microstrips and uploaded to the VNA for automatic de-embedding. The phase

distortion along the sample was compensated numerically using a phase unwrapping technique.

The measured impedance dispersions were fitted with multi-pole dispersion models available

in CST Studio Suite and followed the Kramers-Kronig relations. Recently, it has been shown

that conventional impedance models [37,38] cannot accurately reproduce impedance response

in the transition from MHz to GHz [39]. Thus, these models have limited practical value in

modelling the microwave response in free space. However, with our reliable impedance

measurement technique, it would be possible to realise a hybrid approach [40], where the

experimental surface impedance is used to numerically solve the scattering problem of an

individual wire inclusion without considering its complex magnetic domain structure [41].

Such approach will enable designing wire-filled composites with desirable microwave

properties and predict their microwave response under external stress/temperature/field stimuli.

2. PCB measurement and calibration cells

We have explored two types of PCB measurement cells, straight and dogbone, shown

in Fig. 1. A cell consists of two microstrips on one side of the board, and a continuous copper

ground plane on the opposite side (Fig. 1a). The microstrips are soldered to SMA connectors

at the edge of the PCB. A straight wire sample is placed in the gap between the microstrips and

connected to them with conductive silver paint, which solidifies without additional heating.

Rogers’s composite materials [42] are widely used for high-frequency PCB designs due to their

stable and isotropic dielectric properties with negligible temperature drift and low loss. Our

boards were made of RO4003-C composite with a thickness of 0.812 mm and dielectric

constant Dk = 3.55 over a broad frequency range and low dielectric losses. To calculate the

microstrip width, we used the online microwave calculator available on Rogers’ website. For

the chosen Dk and thickness, the width of the microstrips was calculated as 1.742 mm,

# 60 Accepted Manuscript

133 | providing a characteristic impedance close to 50 Ω over the whole frequency range. Further
134 | rules for designing waveguide structures can be found in [33].
135 | A simpler straight PCB cell allows the application of external stimuli such as magnetic
136 | field and heating (Fig. 1b). Heating can be realized by local blowing of samples with hot air.
137 | Typical boards can withstand prolonged heat up to 200 degrees. Ceramic substrates have
138 | practically no temperature restrictions. The main problem remains the removal of heat from
139 | the rest of the board, where the coaxial connectors are located. The easiest way to control the
140 | temperature is with thermocouples at one or more reference points, where it can be measured
141 | with an accuracy of fractions of a degree. The closeness of the wire temperature to those
142 | measured at the reference points will be guaranteed by the uniformity of the blowing flow, the
143 | incomparably greater heat capacity of the board, and the high thermal conductivity of the wire.
144 | The dogbone cell (Fig. 1c) has protrusions for gripping by the clamps of the stress machine
145 | that allows the transfer of tensile stress to the sample through the elastic deformation of the
146 | PCB. After the sample was connected to the microstrips, it can be additionally glued to the
147 | board for more efficient stress-transfer. Simultaneously with stretching, the sample can be
148 | exposed to magnetic field and heating. Each cell type has a fixed microstrip length, and the gap
149 | between microstrips can be varied to accommodate samples of varying lengths (10 and 20
150 | mm). The length of the sample should be much longer than the end segments involved in the
151 | connection to the microstrips (1 − 2 mm each from each side). Measurement of shorter wire
152 | samples would solve the problem of phase incursion along them [35,36]. However, it may
153 | introduce significant distortions due to the magnetic domains at the wire ends, as well as
154 | increasing uncertainty in the length outside the contact pads.

155

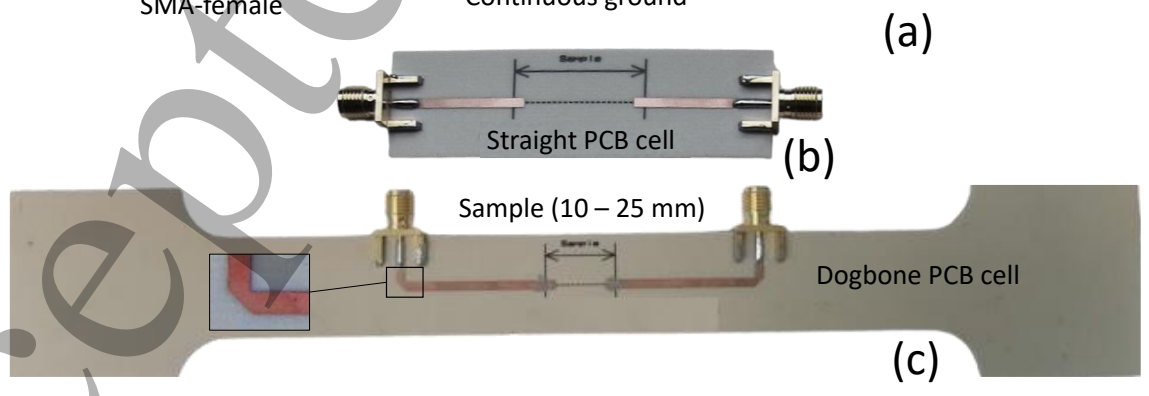
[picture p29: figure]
Dogbone PCB cell; Sample (10 – 25 mm); Straight PCB cell

156 | Fig. 1. PCB cells used for the impedance measurements (a) schematic diagram of the PCB
157 | cell; (b) straight cell; (c) dogbone cell

158

dielectric
Continuous ground
Wire sample | Microstrip Silver paint

SMA-female

Page 5 of 28 | AUTHOR SUBMITTED MANUSCRIPT - MST-116463.R1

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
# 60 Accepted Manuscript

Phase and amplitude distortions, including multiple reflections introduced by the

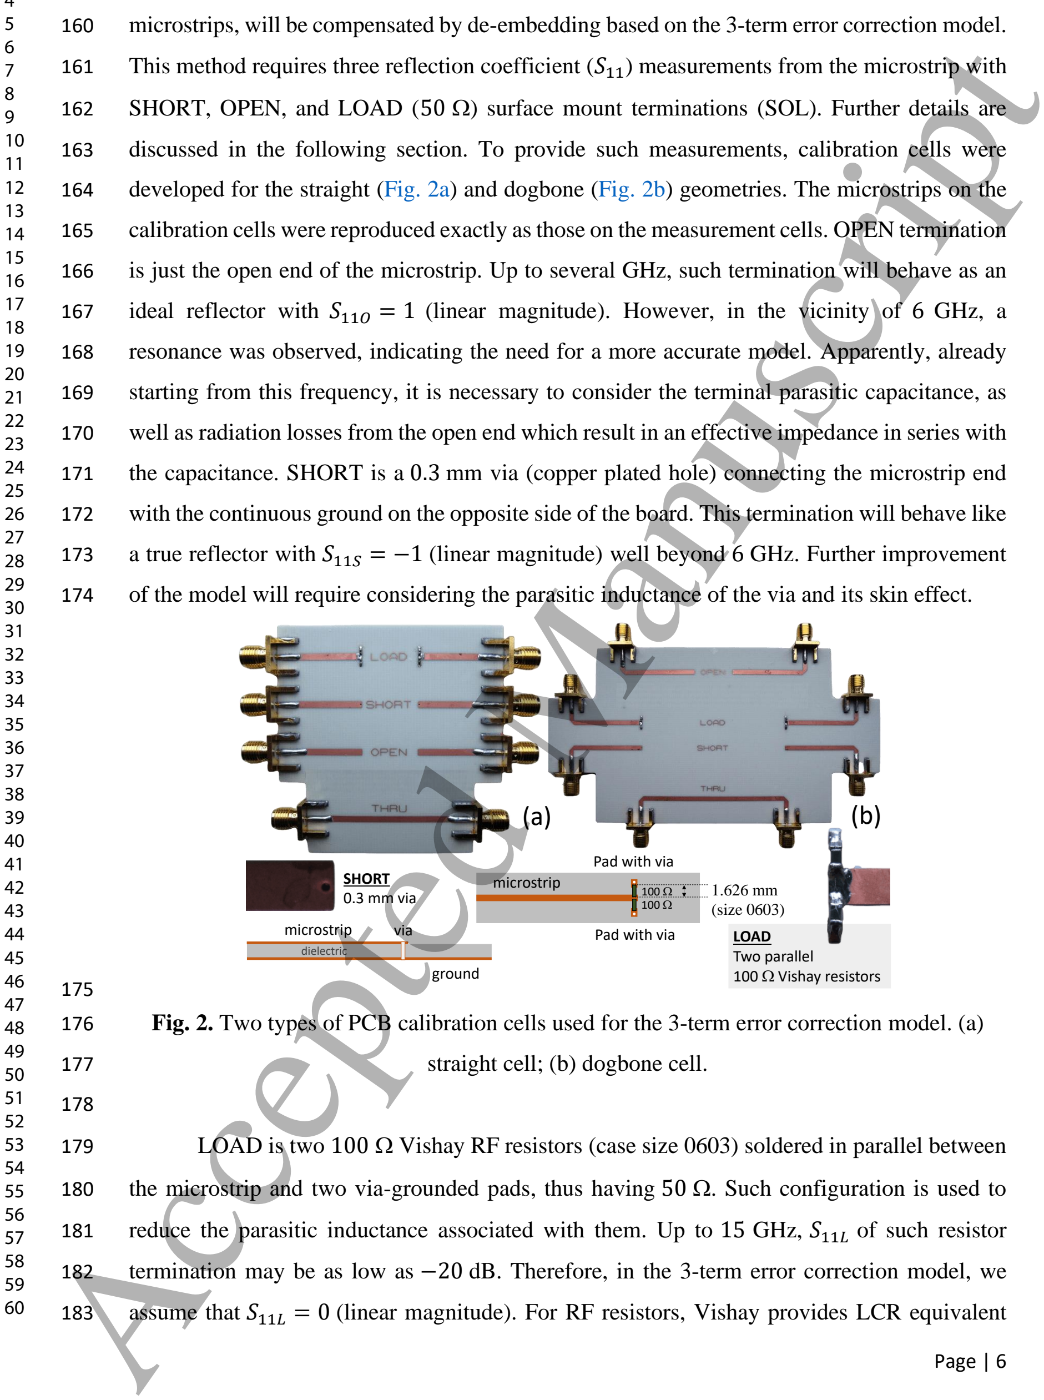
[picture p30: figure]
SHORT 0.3 mm via; LOAD; microstrip; via; Pad with via; (size 0603); 60 Accepted Manuscript

microstrips, will be compensated by de-embedding based on the 3-term error correction model.

This method requires three reflection coefficient (S11) measurements from the microstrip with

SHORT, OPEN, and LOAD (50 Ω) surface mount terminations (SOL). Further details are

discussed in the following section. To provide such measurements, calibration cells were

developed for the straight (Fig. 2a) and dogbone (Fig. 2b) geometries. The microstrips on the

calibration cells were reproduced exactly as those on the measurement cells. OPEN termination

is just the open end of the microstrip. Up to several GHz, such termination will behave as an

ideal reflector with S11O = 1 (linear magnitude). However, in the vicinity of 6 GHz, a

resonance was observed, indicating the need for a more accurate model. Apparently, already

starting from this frequency, it is necessary to consider the terminal parasitic capacitance, as

well as radiation losses from the open end which result in an effective impedance in series with

the capacitance. SHORT is a 0.3 mm via (copper plated hole) connecting the microstrip end

with the continuous ground on the opposite side of the board. This termination will behave like

a true reflector with S11S = −1 (linear magnitude) well beyond 6 GHz. Further improvement

of the model will require considering the parasitic inductance of the via and its skin effect.

Fig. 2. Two types of PCB calibration cells used for the 3-term error correction model. (a)

straight cell; (b) dogbone cell.

LOAD is two 100 Ω Vishay RF resistors (case size 0603) soldered in parallel between

the microstrip and two via-grounded pads, thus having 50 Ω. Such configuration is used to

reduce the parasitic inductance associated with them. Up to 15 GHz, S11L of such resistor

termination may be as low as −20 dB. Therefore, in the 3-term error correction model, we

assume that S11L = 0 (linear magnitude). For RF resistors, Vishay provides LCR equivalent

Two parallel
100 Ω Vishay resistors

dielectric
ground

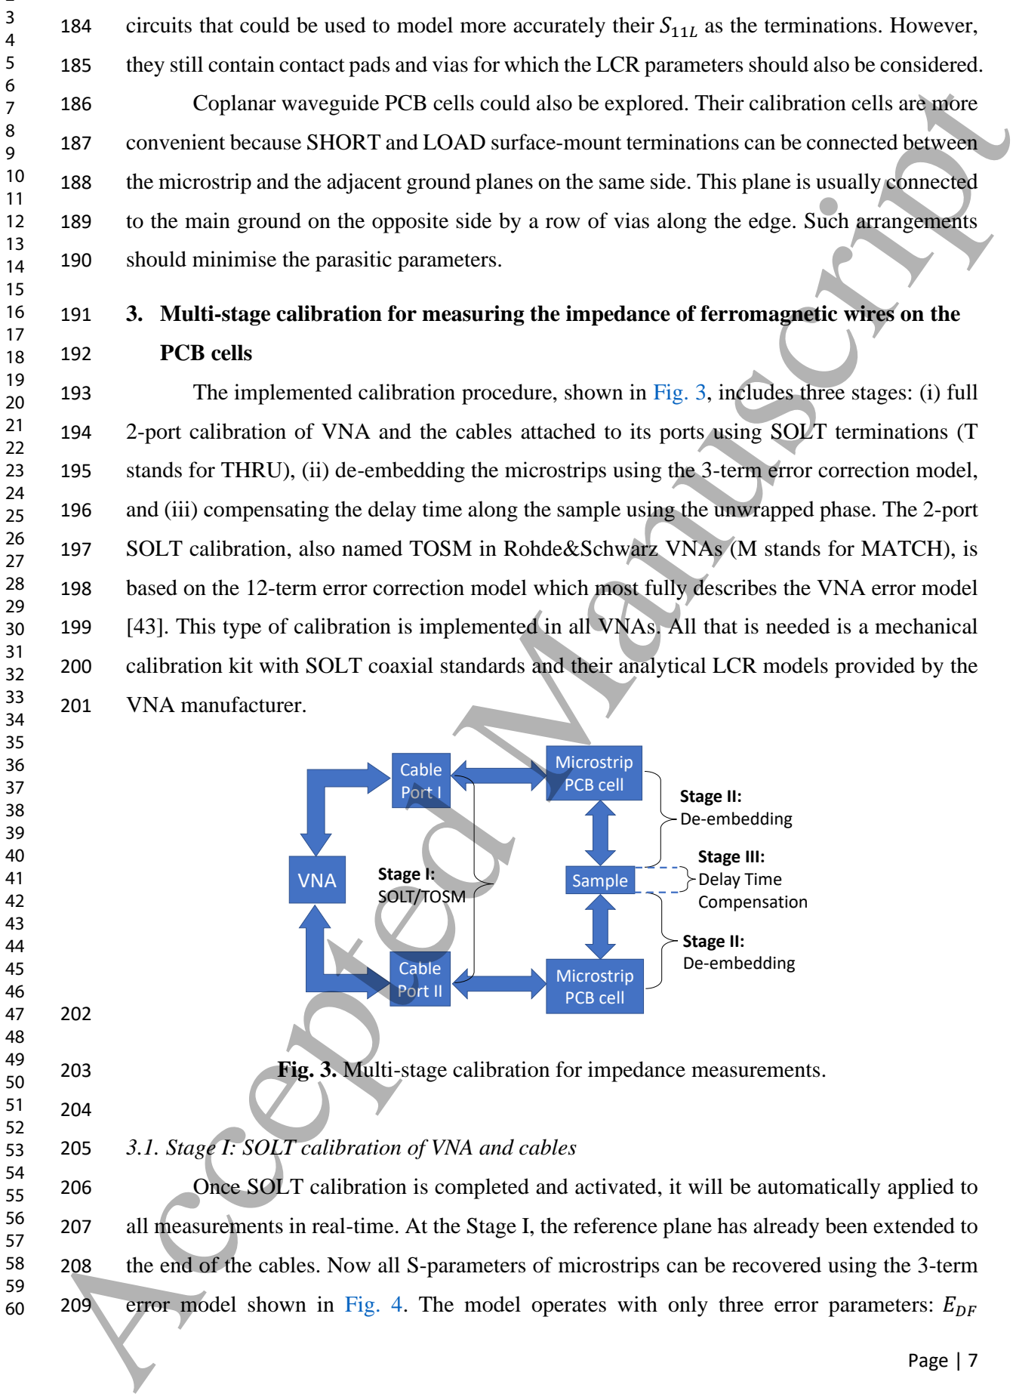
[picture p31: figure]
should minimise the parasitic parameters.; PCB cells; VNA manufacturer.; VNA; Cable Port I; Microstrip PCB cell; Sample; Cable; Port II; Microstrip; PCB cell; Stage I: SOLT/TOSM; Stage II: De-embedding; Stage III: Delay Time Compensation; 60 Accepted Manuscript

184 | circuits that could be used to model more accurately their S11L as the terminations. However,
185 | they still contain contact pads and vias for which the LCR parameters should also be considered.
186 | Coplanar waveguide PCB cells could also be explored. Their calibration cells are more
187 | convenient because SHORT and LOAD surface-mount terminations can be connected between
188 | the microstrip and the adjacent ground planes on the same side. This plane is usually connected
189 | to the main ground on the opposite side by a row of vias along the edge. Such arrangements
191 | 3. Multi-stage calibration for measuring the impedance of ferromagnetic wires on the
193 | The implemented calibration procedure, shown in Fig. 3, includes three stages: (i) full
194 | 2-port calibration of VNA and the cables attached to its ports using SOLT terminations (T
195 | stands for THRU), (ii) de-embedding the microstrips using the 3-term error correction model,
196 | and (iii) compensating the delay time along the sample using the unwrapped phase. The 2-port
197 | SOLT calibration, also named TOSM in Rohde&Schwarz VNAs (M stands for MATCH), is
198 | based on the 12-term error correction model which most fully describes the VNA error model
199 | [43]. This type of calibration is implemented in all VNAs. All that is needed is a mechanical
200 | calibration kit with SOLT coaxial standards and their analytical LCR models provided by the
203 | Fig. 3. Multi-stage calibration for impedance measurements.
205 | 3.1. Stage I: SOLT calibration of VNA and cables
206 | Once SOLT calibration is completed and activated, it will be automatically applied to
207 | all measurements in real-time. At the Stage I, the reference plane has already been extended to
208 | the end of the cables. Now all S-parameters of microstrips can be recovered using the 3-term
209 | error model shown in Fig. 4. The model operates with only three error parameters: EDF
Page 7 of 28 | AUTHOR SUBMITTED MANUSCRIPT - MST-116463.R1

1
2

(directivity forward), ERF (reflection tracking forward), and ESF (source mismatch forward).

The actual reflection S11A produced by a termination connected to the microstrip end is

entangled into S11M measured from the coaxial connection soldered to the PCB:

S11M =

b1
a1

= EDF +

ERFS11A
1−S11AESF

(1),

where a1 and b1 represent input and output signals, respectively. By measuring three

reflections on the PCB calibration cell, where the microstrip is terminated with non-coaxial

SOL, it becomes possible to find EDF, ERF, and ESF, and then recover all S-parameters of the

microstrip. Note that during these measurements the calibration cell is connected to the VNA

and the cables which have been already calibrated at Stage 1.

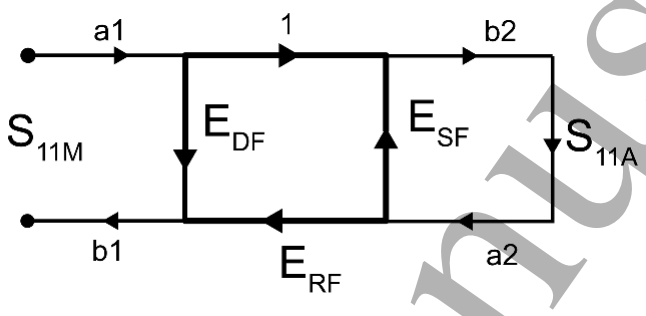
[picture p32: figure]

Fig. 4. 3-term error correction model. a1,2 and b1,2 represent input and output signals,

respectively.

In Eq. (1), we have three unknowns EDF, ERF, and ESF which can be found from S11M

measured from the three known termination standards SHORT (S11A → S11S 224 | ), OPEN (S11A →
S11O), and LOAD (S11A → S11L 225 | ):

{

S11MS = EDF +

ERFS11S
1−S11SESF

S11MO = EDF +

ERFS11O
1−S11OESF

S11ML = EDF +

ERFS11L
1−S11LESF

(2).

After getting rid of the denominators, the system of Eq. (2) becomes linear with respect to three variables: x = EDF, y = ESF, and z = (ERF − EDFESF):
{
EDF + S11MSS11SESF + S11S(ERF − EDFESF) = S11MS

EDF + S11MOS11OESF + S11O(ERF − EDFESF) = S11MO

EDF + S11MLS11LESF + S11L(ERF − EDFESF) = S11ML

(3).

For our terminations on the PCB calibration cells, we assumed S11S ≡ −1, S11O ≡ 1, and

S11L ≡ 0 for the whole frequency range. If more accurate LCR models are available for the

terminations, the interpolated values can be used. Solving Eq. (3) numerically for each

frequency point within the sweep range set at SOLT of the VNA, all S-parameters of the
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

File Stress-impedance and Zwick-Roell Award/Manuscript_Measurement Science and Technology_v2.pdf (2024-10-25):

Published: Measurement Science and Technology 31, p. 025901 (2020) | DOI: 10.1088/1361-6501/ab4556

### Novel broadband measurement technique on PCB cells for the field-and stress-dependent impedance in ferromagnetic wires

Yujie Zhao,

1) Yunfei Wang,¹⁾ Diana Estevez,¹⁾ Faxiang Qin,¹⁾ Huan Wang,¹⁾ Xuefei Zheng,¹⁾ Dmitriy Makhnovskiy¹,2)

, and Huaxin Peng,¹⁾

1
Institute for Composites Science Innovation (InCSI), School of Materials Science & Engineering, Zhejiang

University, 38 Zheda Road, Hangzhou, 310027, PR China.

2Sensing Materials Technology Ltd, 44 St. Michaels Close, Plymouth, Devon, PL1 4RX, United Kingdom.

Abstract

The lack of broadband impedance measurements has restricted the potential capabilities of

ferromagnetic wire composites which have been mainly evaluated through theoretical impedance

calculated from existing models without considering wire domain microstructure. Here, we

developed an accurate method for measuring the impedance of ferromagnetic wires in a wide

frequency range from 100 kHz up to 15 GHz under magnetic and stress stimuli. The broadband

measurements were ensured by a more accurate microwave calibration on the PCB cell extending

the reference planes up to the wire sample ends and by compensating the sample waveguide

properties using the phase unwrapping technique proposed in this work. In addition, a specially

designed dogbone PCB measurement cell allowed both magneto-impedance and stress-impedance

measurements efficiently transferring the tensile stress from cell to the wire sample fixed onto it.

The measured wire impedance can be then recalculated into the surface impedance which

constitutes the boundary condition in the antenna equation describing the microwave scattering

properties of a wire. The developed approach will make it possible to build a practically predictive

scattering theory in composite materials with embedded wire inclusions and thus their

implementation in real-world applications such as remote stress monitoring.

Keywords: magneto-impedance, stress-impedance, ferromagnetic resonance, surface impedance, microwave

scattering, antenna equation, microwave calibration, tensile strain, composite materials, remote stress monitoring.

E-mails:contact@sensmattech.co.uk.

Introduction

Since its re-discovery in 1994, the magneto-impedance (MI) effect which refers to the change

in ac electrical impedance due to the application of a static magnetic field has been the focus of

much research interest. Main studies have been conducted in glass-coated microwires, where the

strongest MI effect was generally observed leading to the development of magnetic field/stress

sensors at MHz frequencies [1-6] and microwave tunable composites incorporating such wire

inclusions.[7-10] However, due to the lack of broadband measurements the microwave properties

of microwire composites have been evaluated merely from the theoretical impedance calculated

from existing models [8,10-12] without considering microscopic magnetic structure of wire

inclusions. Such issue presents a limitation for realization of practical applications in such

composites, e.g. in remote stress monitoring where a proper interpretation of the distribution of

local stresses becomes imperative. The situation could be reversed by developing a predictive

model via existing formalisms of electromagnetism of continuous media that includes the material

constitutive parameters such as dielectric properties of the hosting medium and magnetic and

conductive properties of wires. In this paper, we develop a robust measurement setup that allows

determining the wire impedance in the presence of magnetic field and stress stimuli in a wide

frequency range. The impedance obtained from the accurate measurements can be then

recalculated into surface impedance delivering the boundary conditions required to calculate the

composites microwave response using the antenna equation. Such strategy also enables to avoid

the consideration of the complex magnetic structure of the wire, which restricts the accurate

modelling of the impedance in a broad frequency range. Our results constitute the basis for the

development of a scattering theory in free space that would allow the full certification of

ferromagnetic microwires as a class of functional fillers for microwave applications.

Integration of the tensile stress and high-frequency impedance measurements

In attempt to implement high-frequency impedance measurements in the presence of tensile

stress, one is confronted with contradictory requirements. On the one hand, a high-frequency

excitation requires special waveguide conditions to ensure the impedance matching along the

whole measurement track. On the other hand, standard waveguide or coaxial measurement

techniques exclude any possibility of a controllable stress transfer to the wire sample. The

measurement setup we propose in the present work (Fig. 1(a,b)), can be used both for the magneto-

impedance (MI) and stress-impedance (SI) measurements. It comprises Z5.0 TN Zwick Roell

stress machine 5 kN, Helmholtz magnetic coil, power amplifier, dogbone PCB measurement cell,

PCB calibration cell, LaVISION optical camera for the strain control, and three Rohde&Schwarz

devices: ZNB20 Vector Network Analyzer (VNA) 20 GHz 2-port, HMF 2550 Function Generator

(FG), and HMC 8012 Digital Multimeter (DMM). Synchronous operation of VNA, FG, and

DMM, connected by LAN to a PC, is controlled by a LabVIEW program. All the devices are

mounted on the height-adjustable trolley to allow its relocation for different experimental

arrangements.

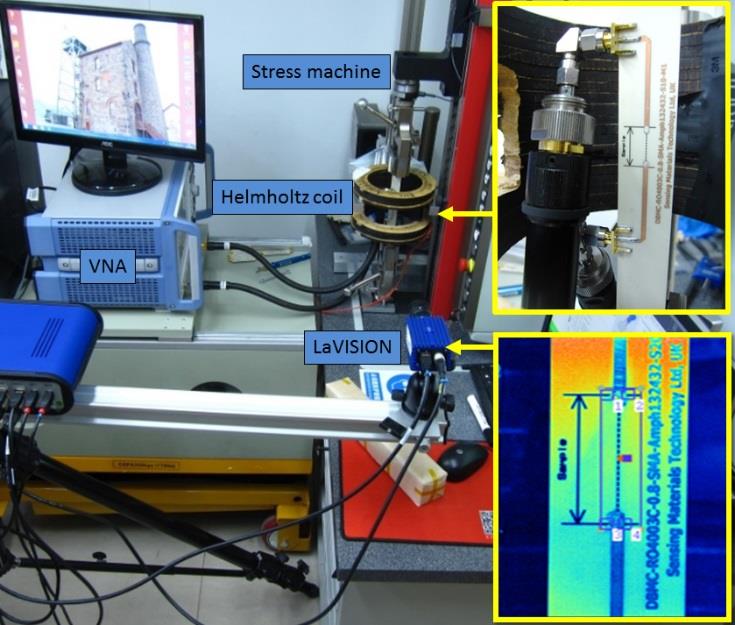
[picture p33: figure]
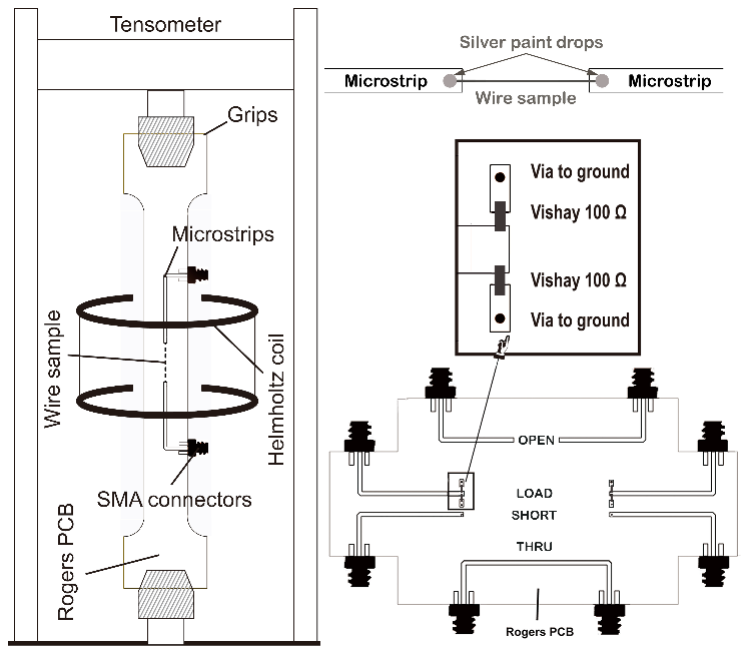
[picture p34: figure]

FIG. 1. Stress-impedance measurement setup (a) and its schematic diagram (b) showing the

dogebone PCB measurement cell and the PCB calibration cell.

A dogbone PCB measurement cell has a continuous copper ground layer on one side of the

board and the L-shape 50 Ω microstrips on the other one. The microstrips are terminated with

SMA connectors which enabled coaxial cable connection with VNA. The wire sample is placed

onto PCB in the gap between the microstrips (Fig. 1(b)) and connected to their ends by a conductive silver paint. The dogbone shape of PCB and its ductility allow a graduate stress transfer

from the machine grippers to the wire sample. We used Rogers’ RO4003C material with the

thickness 0.812 mm and the dielectric constant ~3.8 in a wide frequency range. The 1.78 mm

width of microstrips, providing the 50 Ω characteristic impedance, was calculated using Rogers’s

microwave impedance calculator MWI 2017. The sample gap between the microstrips varied from

10 to 25 mm. A 2 mm space from the end of the microstrips was reserved for the wire electrical

connection.

For accurate network measurements, it is necessary to propose a calibration technique that

extends the reference planes from the cable coaxial connectors to the microstrip ends. We designed

and built the PCB calibration cell realising SOLT calibration technique [13] in a wide frequency

range from kHz up to 15 GHz. The PCB calibration cell, shown in Fig. 1(b), was made of the same

RO4003C. The shape, length, and width of its microstrips must be identical to those on the

dogbone PCB measurement cells. The SHORT and OPEN termination standards were made of the

short grounded (through a via) and open microstrip ends respectively. The LOAD standard was

made of two RF 100 Ω surface mounted resistors (Vishay resistor, size 0402) connected in parallel

to the ground plane through the vias to provide the 50 Ω termination. Such configuration is used

to reduce the parasitic inductance of the resistors. The THRU standard was made by connecting

two microstrips together without the sample gap. When using this calibration cell with a VNA, the

“ideal calibration kit” (option available in modern VNAs) can be chosen assuming that S11-

parameter (reflection coefficient) measured from SHORT, OPEN, and LOAD takes the values −1,

1, and 0 respectively. More realistic models for the SOL standards, considering their LC-paraments

and delay times, could provide even better accuracy at higher GHz frequencies.

After the SOLT calibration on PCB, the reference plane will be shifted to the microstrips ends.

The impedance Z of a wire sample placed onto PCB between the microstrips could be calculated

from the measured transmission coefficient S21 using the well-known equation: Z = 100 × (1 −

S21)/S21. However, this equation assumes that S21 is measured from a lumped element. This is

not the case for a wire sample at the frequencies beyond a hundred of MHz because it represents

by itself a waveguide over the ground plane. To extract purely impedance properties, the phase

incursion along the sample caused by the wave propagation must be compensated. To do so, the

phase of S21(ω), measured through the wire sample at zero magnetic field and stress, was first

unwrapped, see Fig. 2, and then approximated by a linear trend line ωa + b within a frequency

interval where the phase has minimum non-linear distortions.

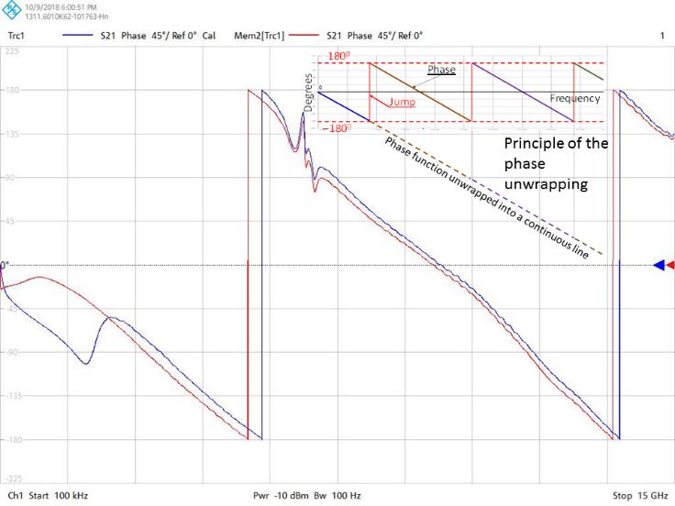
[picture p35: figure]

FIG. 2. The phase of S21(ω) measured in a ferromagnetic wire at zero and a large magnetic field.

The unwrapped phase at zero field and stress is used for calculating the delay time along the wire

sample.

Thus, the delay time Δt caused by the wave propagation along the sample equals |a|. For the

calculation of Z , S21(ω) in the equation above must be replaced with S̄ 21(ω) =

S21(ω)exp( iωΔt), where i is the imaginary unit. In the proposed measurement technique, special

care must be taken to minimize uncertainties associated with the contact pads on the microstrips

for the wire sample. The dimension of the pads must be much smaller than the shortest wavelength

propagating along the microstrips. Also, they must be much smaller than the gap for the wire

sample thus minimising the phase uncertainties in the phase unwrapping technique.

For MI measurements, a DC offset voltage from FG is applied to the power amplifier to feed

the Helmholtz coil. The actual voltage (after amplification) applied to the coil is measured by

DMM. Its reading is passed to the program to be recalculated into the field using the coil calibration

coefficient (field/voltage). After applying a DC offset voltage, the program is paused to allow the

full coil charge/discharge during

>> LR/
, where
L

and
R

are the coil inductance and resistance

respectively. After the pause (ms), VNA is activated to measure
21 S

in discrete frequency points

in single sweep. The transmission coefficient measured in discrete frequency points is passed as

an array to the LabVIEW program, where it is corrected to compensate the sample phase incursion

and converted into the impedance. After the sweep, the measurement process is repeated with the

next field point.

For SI measurements, between successive strain steps, in a single sweep VNA measures
21 S

in discrete frequency points over a wide range for a specified magnetic field as a bias. During this

sweep, the displacement between the machine grippers is kept constant. Measuring the dispersion

of

21 S
for a large number of bias fields and then transferring this data to PC may take several

minutes. During this time, the local strain near the sample may slightly release due to viscous flow

of PCB. For controlling the real strain applied to the sample, we used the digital imaging

correlation technique (DIC) provided by LaVISION optical camera. With just a grey color scale

for a pixel intensity, the digital camera creates a unique signature for each point of the image. A point signature is correlated by neighboring points. When the image is being deformed, these point

signatures move from their original positions revealing local vector displacements. The magnitude

of a local displacement can be visualized using a 256-level color graduation (Fig. 1(a)). So,

selecting a certain direction, the color mapping of the displacement spatial distribution along this

direction can be created. For tracking a stretching of the gap, one needs to select some small

reference areas at its edges. The program will automatically identify the reference points in these

areas. When applying the tensile stress to the PCB board, the difference between the displacements

of the reference points will give the absolute stretching of the gap.

Broadband magneto-impedance and stress-impedance measurements

In order to illustrate the developed technique for the MI and SI measurements in a wide

frequency range, we used a glass-coated ferromagnetic wire with the alloy composition (wt%)

Co68.7Fe4Si11B13Ni1Mo2.3 produced by the Taylor-Ulitovsky method.[14] The wire had a metal

core diameter of 18.6 µm and total diameter of 21.6 µm. The sample gap in the dogbone cell was

25 mm. Fig. 3 shows characteristic features of the MI behavior measured at the MHz and GHz

frequencies. For MHz frequencies, the impedance field dependencies have two symmetrical

maximums within the field scanning range. Increasing the frequency, the impedance magnitude

also increases. In the transition from the MHz to GHz frequencies, a rather complex scenario of

changing of the MI curves is observed. Starting from some frequency in the upper MHz range

(~700 MHz for the wire in Fig. 3), the inflection points will gradually develop on the MI curves

before the maximums. Increasing the frequency further, the maximums will grow to a certain value

and simultaneously shift to the region of larger fields, while the inflection points will reduce their

impedance values. When the maximums already shifted outside the field scanning region, MI curves will take shapes with two distinct slopes. Further increase in frequency will result in the

slow slopes becoming almost the horizontal lines. This final shape will be saved for higher

frequencies in the GHz range with further decrease of the impedance magnitude. These subtle

transitions in magneto-impedance curves have not been accurately tracked in previous reports.

The behavior of MI shown in Fig. 3 can be qualitatively reproduced using the MI model

proposed in Ref. 10. There, the magnetization vector M⃗
0 of the homogeneously magnetized shell

of the wire is rotated by the external magnetic field Hex according to the Stoner-Wohlfarth model

[15] with the density of magnetostatic energy U(φ) = −M0((HK/2) cos²
( α − φ) +

Hex cos( φ)), where α ≤ 90

0
is the anisotropy angle measured from the wire axis, φ is the

equilibrium angle of M⃗

0 in the presence of Hex (φ = α for Hex = 0), M0 = |M⃗
0|, and HK is the

anisotropy field. The ac magnetic susceptibility, calculated from the Landau-Lifshitz equation,

allows one to solve the Maxwell equations inside the wire and thus find the wire surface impedance

tensor. One of its diagonal components can be expressed through the wire impedance Z as

explained in the next section. The shape of the MI curves calculated in the frame of this model

approach is very sensitive to the value of the spin-relaxation parameter, which should be chosen

sufficiently small to reproduce the scenario of transformations shown in Fig. 3. The radial

distribution of the magnetic properties might also contribute to the observed transformations. To

solve these questions we require a separate research which will be conducted elsewhere. For now

we have an accurate measurement technique that allows us to confidently discuss these effects.

The splitting of the MI curves observed at large positive fields after the full field scan (see

Fig. 3), especially for 2 and 7 GHz is also another issue to take into consideration. These splits

might be taken as measurement uncertainties, but most likely they are caused by the magnetization

reversal processes in the inner core with the longitudinal magnetization. The conductivity through the inner core has never been included into the previous MI models. Measurements of MI in larger

magnetic fields might clarify this question.

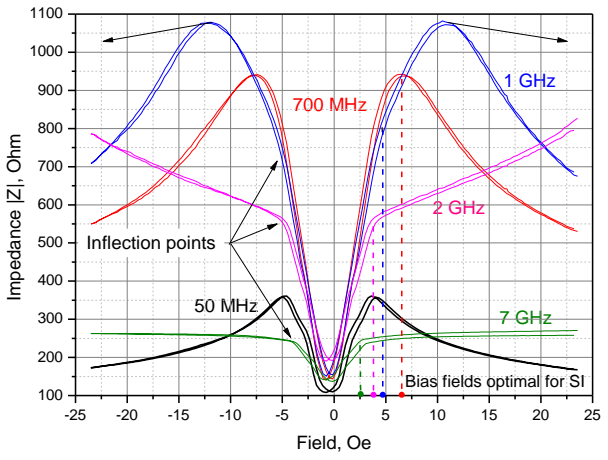
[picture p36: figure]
50 MHz; 7 GHz; 2 GHz; 700 MHz; 1 GHz; 1100 Impedance |Z|, Ohm; Field, Oe; Inflection points; Bias fields optimal for SI

FIG. 3. Field dependencies of the impedance in the MHz and GHz ranges. A complex scenario of

changing of the MI curves has been revealed in the transition from the MHz to GHz frequencies.

The same as MI, the stress sensitivity of the impedance is due to the rotation of the

magnetization in the circularly magnetized shell of the wire. Staying within the Stoner-Wohlfarth

magnetostatic model, the anisotropy field HK of the shell can be expressed through the total tensile

stress σ = σres + σex applied to the wire: HK = 3λσ/M0, where σres is the residual tensile stress

induced during the wire casting process, σex is the external tensile stress, and λ is the

magnetostriction constant. Since the maximums of MI occur at Hex = ±HK, applying an external

tensile stress will result in widening of the MI curves, while the impedance in zero bias field will

remain unchanged for any frequency as shown in Fig. 4. Thus, to realize SI behavior in a wire with

a circumferential anisotropy, an external magnetic bias field must be applied. The complex
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

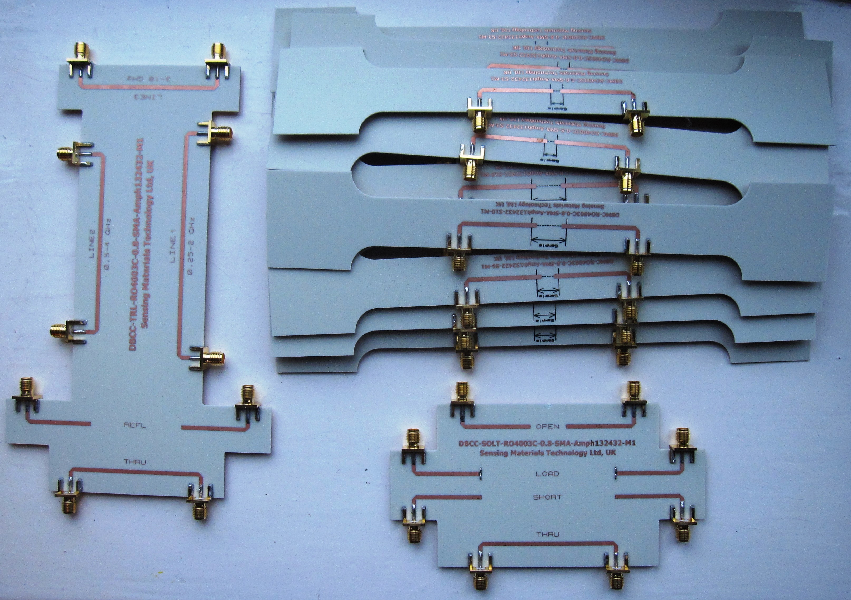
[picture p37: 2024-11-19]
Rogers' PCB cells/Ready cells/2_DogBone cells and TRL&SOLT calibration boards.JPG
